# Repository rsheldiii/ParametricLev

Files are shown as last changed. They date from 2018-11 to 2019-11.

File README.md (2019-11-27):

# ParametricLev, A Parametric Acoustic Levitation Device

video of acoustic levitator test (https://www.youtube.com/watch?v=uWjfwIOMlY8)

After coming across the Instructables for [acoustic levitators](https://www.instructables.com/id/Acoustic-Levitator/) and [tractor beams](https://www.instructables.com/id/Acoustic-Tractor-Beam/) from UpnaLab, I was determined to make my own. I wanted a little more control over how the device looked, so I set about making a parametric version. Generating a new enclosure still has some manual tweaking, but it's much easier now!

# Acoustic Levitation?

I encourage you to explore the instructables linked above, but the tl;dr of acoustic levitation is by manipulating sound waves high enough that the human ear can't hear them, you can create high pressure and low pressure pockets that will force objects to move in a predictable pattern. In our case, we are setting up two transducer arrays in direct opposition to each other, creating a standing wave that will allow us to place objects at the nodes.

# Differences from the original design

## BigLev

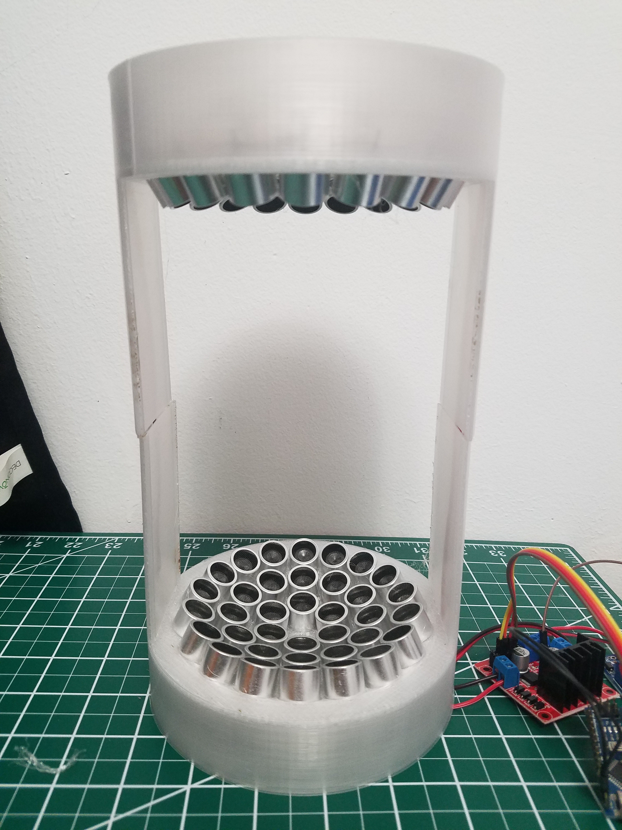
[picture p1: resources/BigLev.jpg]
picture of BigLev


Like BigLev in the instructable, I ended up going with 16mm transducers, since they are more powerful and they were also cheaper than any 12mm transducers I could find. I bought 8 of [these](https://www.amazon.com/gp/product/B01FDGTXT4/ref=oh_aui_detailpage_o00_s00?ie=UTF8&psc=1) for ~$8 a pop, for a total of 80 transducers. If you so desire, this allows you to build a BigLev, a MicroLev, and a NanoLev (72 + 6 + 2).

The original acoustic levitation instructable has you order a power supply that can discretely switch between voltages. This works well, but my transducers support up to 30 volts, so I ended up using the variable step-up transformer from the tractor beam instructable. 30 volts is overkill for most applications (since voltage is mostly related to how dense a material you can levitate) but being able to precisely tune the voltage level is great for getting things to stay stable.

## MicroLev

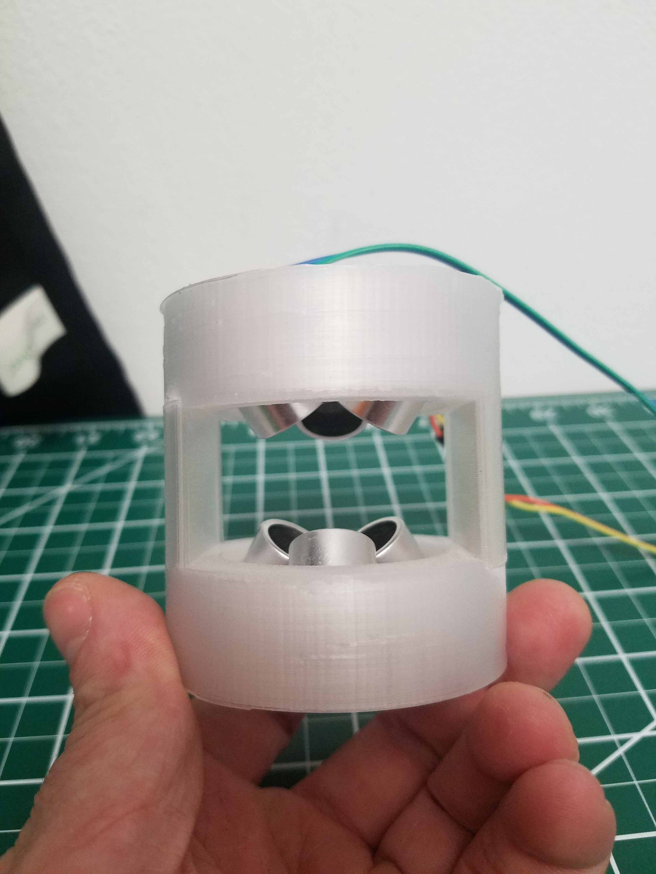
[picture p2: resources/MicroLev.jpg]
picture of MicroLev


MicroLev isn't featured in the original isntructable, but I wanted something simpler to test the wiring on before scaling all the way up. 6 transducers is a little hard for the nano to drive, so it can just barely levitate styrofoam without a motor controller. You might be able to increase this power by hooking up each transducer to a different pin and modifying the code, since you won't be reliant on the current output of a single pin to drive the transducers, but remember that arduino pins are connected to buses which themselves have a max current draw, so you'll have to be crafty about it. You can sidestep all of this however and just wire the MicroLev like you would the BigLev here or in the original instructable, allowing you to levitate popcorn pieces and probably a few other things.

## NanoLev

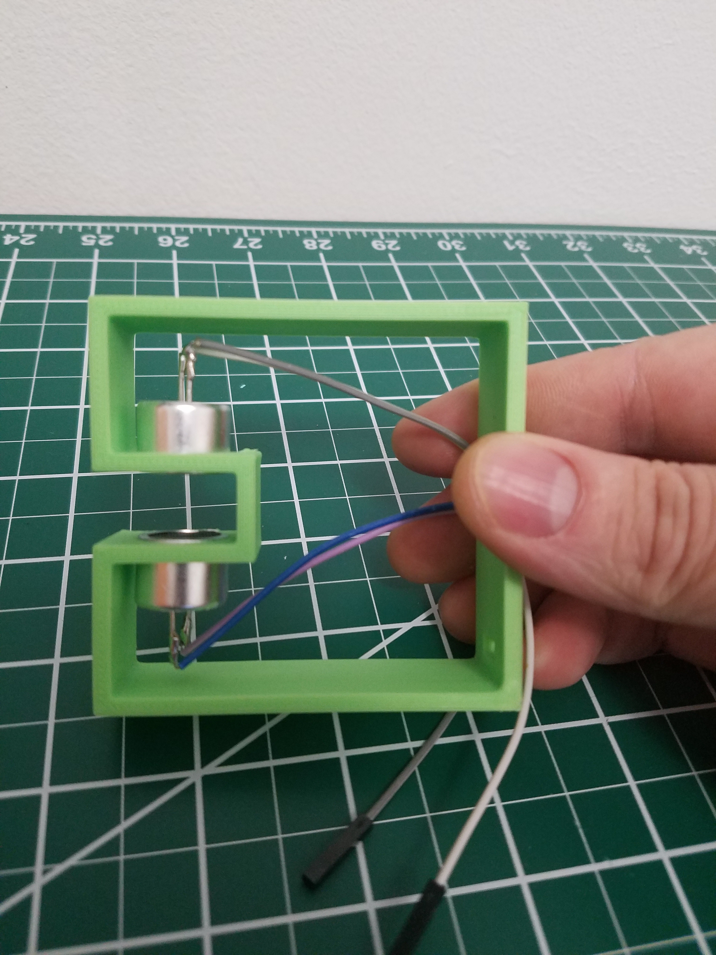
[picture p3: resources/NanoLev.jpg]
picture of NanoLev


the NanoLev is a tiny WIP enclosure for the two-transducer device from the instructable. You'll have to find something to support the Nano, but it works ok!

# How to assemble

This is only a list of the changes to the instructions and gotchas I encountered, so please reference the original instructable while you assemble the design. I may write up a full build log later, but as it stands the differences are pretty minimal

## BOM

* l298N, https://www.amazon.com/gp/product/B01CC8XI60/
* Arduino nano, https://www.amazon.com/gp/product/B00Q9YBO88/
* DC/DC Voltage Transformer, https://www.amazon.com/gp/product/B00J03PBW0
* 12V 3A wall wart, https://www.amazon.com/gp/product/B07CWVFGNN
* 72 16mm 40khz transducers, https://www.amazon.com/gp/product/B01FDGTXT4/
* bare copper wire, https://www.amazon.com/gp/product/B00E4WL2D4/
* black/red wire, https://www.amazon.com/gp/product/B009VCZ4V8/
* barrel connector, https://www.amazon.com/gp/product/B00T7VOKM2/

## Printing

for the __BigLev__, print two halves, with support. for the __MicroLev__ you need to print the top and bottom; the files come from an earlier design where opposing sides slotted together that unfortunately didn't fit on my 3d printer when scaling up to the BigLev. For the NanoLev, just print the one file; it's a completely different setup than the other designs.

There are some nasty overhangs in the BigLev and MicroLev prints, so make sure you print in whatever material gives you the best overhang performance.

## Transducers

DO NOT SKIP MARKING YOUR TRANSDUCERS. Despite most transducers having a marked 'ground' wire it does NOT correlate to polarity. For most applications this does not matter, but in our case if you place two transducers with opposite polarity next to each other they will destructively interfere, decreasing the power of your device. The direction of the polarity doesn't actually matter, but what _does_ matter is that all transducers are wired the same. I placed the marked leg towards the center, just like the instructable. I created a jig for testing the polarity, which you can glue wires into to make it easier to connect the transducer to the arduino:

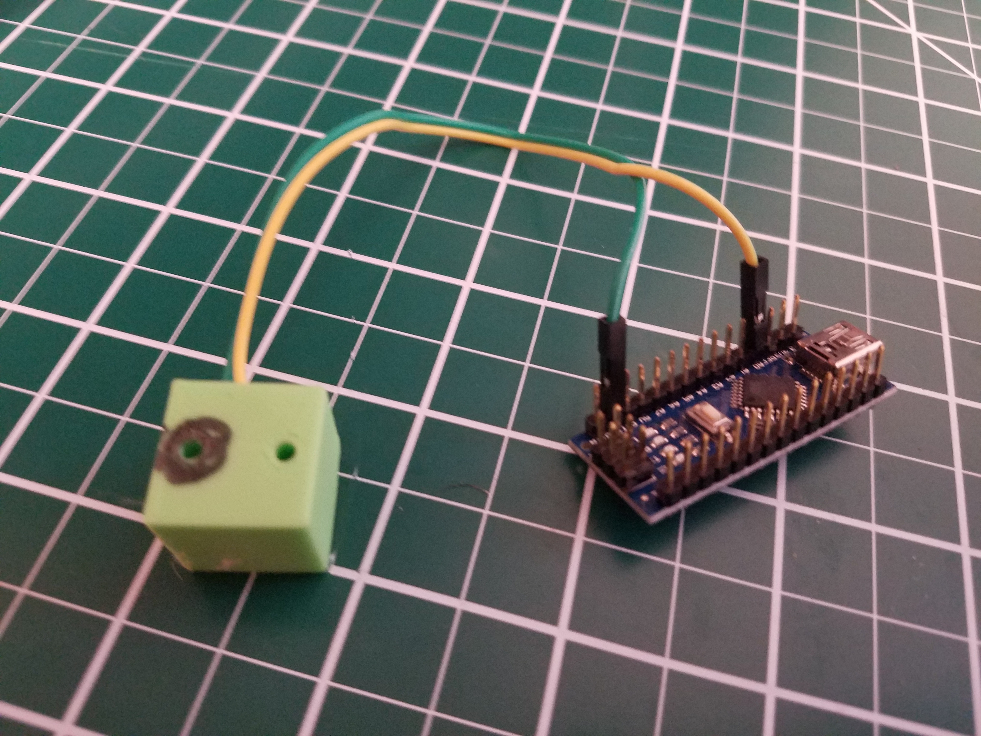
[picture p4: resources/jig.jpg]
picture of wiring jig


Most transducers come in pairs; one transducer is for transmitting waves and the other for receiving. Transmitters are tuned to produce waves based on electrical input, whereas receivers are tuned to produce electrical input based on sounds. While this _sounds_ bad for us, since we are only interested in producing waves, receivers and transmitters can be used interchangeably with a small loss in efficiency. If you can find a source of only transmitters (or transceivers, which are a compromise between the two) by all means, but it really isn't worth any extra money. For peace of mind, I separated my transmitters and receivers and alternated between them when I placed them in the enclosure, so that I wouldn't accidentally place a large amount of them on either half.

## Wiring

I will get better pictures for this later, I promise.

You can by all means follow the original wiring in the instructable, but if you want to use the step-up transformer you'll have to make a few modifications. Wire the actual device as they do in the instructable, and wire it to the l298N driver as they do as well. Since we'll be far exceeding the 12V the controller needs to run its own logic, we'll need to patch in 12V from the wall wart and tell the controller to use that for logic instead of the input voltage. This means you need to take off the jumper, and attach a wire from 12V in it's place. See the brown wire in this picture:

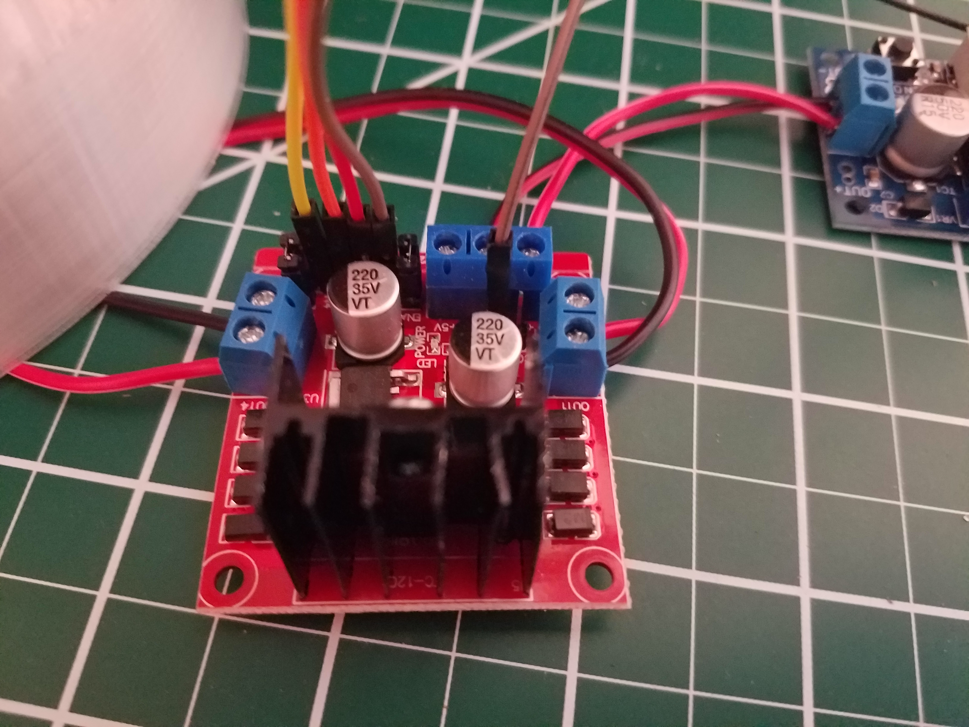
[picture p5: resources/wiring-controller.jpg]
picture of wiring the l298N controller


It is VERY IMPORTANT to put this wire in the correct place, otherwise you might damage the controller or start a fire.

Instead of feeding in electricity directly from the wall wart, the input to the controller comes from the step-up transformer, as you can see in the picture.

The arduino Nano can't handle the voltage we'll be pumping into the controller, so we'll also need to run wires from the barrel connector to the arduino's VIN and GND pins. Otherwise, the wiring is the same as the instructable. Picture reference:

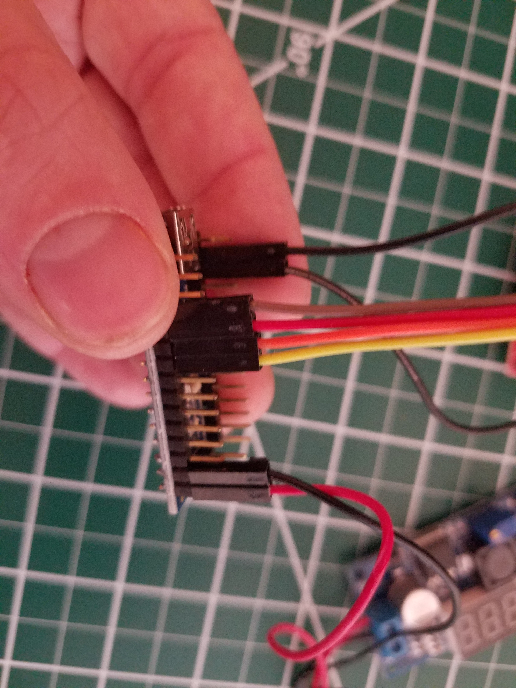
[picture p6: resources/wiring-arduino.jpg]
picture of wiring the l298N controller


after all is said and done, the wiring should look like this:

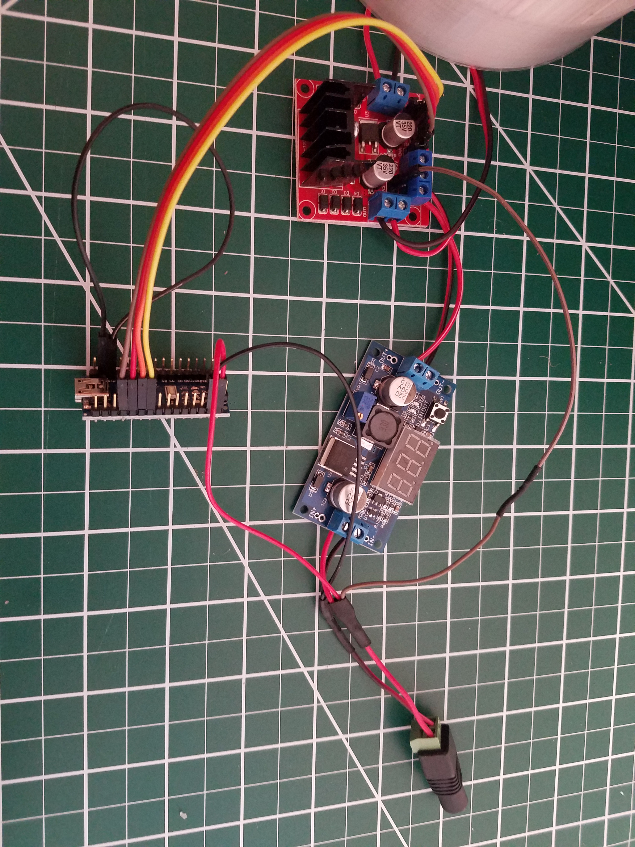
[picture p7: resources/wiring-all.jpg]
picture of wiring the l298N controller


except not as messy

## Programming

Programming on the arduino is exactly the same as in the instructable, just grab their .ino file and use it.

Of note is that an arduino nano is pretty overkill for this application, since all it's doing is creating a 40KHZ signal. The arduino could be replaced by a clock and crystal and some power management circuitry by someone more electrically inclined than I am.

## Using

I find it easiest to use teabag material to place objects, though any sonically transparent material would work fine (wire mesh is probably the best). If your item is spinning rapidly it's an indication that the standing wave is too intense for its density; try decreasing the voltage on the transformer until it slows down.

If you have a resin printer (or are ok with paying Shapeways 7.50 per part), you can get extremely tiny 3d printed models to levitate. The size of the object that can be levitated is a function of half the wavelength, so anything more than ~4.5mm in diameter is too large. Luckily that's just above the minimum size requirements for Shapeways.

## Spacing

I have noticed with my current design that I can get some nasty resonance in the exact middle spot, causing pieces to fall despite them levitating just fine in other spots. I've noticed that changing the distance between the pieces makes this go away, so I think it's a function of the radius of the internal sphere being a multiple, or perhaps an odd multiple, of half the wavelength. I've increased the multiple to 22 but haven't actually tested it yet. If you have similar problems though, you could easily print a tiny piece of the side sponsons and glue it in place, increasing the height. I've included an example shunt in the models directory, but the height of the shunt is probably better found through experimentation.

# Modifying

If you want to use a different amount of transducers or change parameters, you can clone this repository and open up `BigLev.scad` and `src/settings.scad` in OpenSCAD or whatever editor you choose. By modifying variables in `settings.scad`, you can generate a different shape.

The amount of transducers is a function of the area of the section of the sphere generated based off some napkin trig, so if you're looking for a specific amount of transducers you'll have to play around a bit (or you can try refactoring the old code in OldStuff.scad to manually control how many transducers there are). The napkin trig isn't perfect, so sometimes in order to eliminate dead space you'll have to dig into `transducers_for()` in `lev.scad` to get a more fine-tuned result. Still though, the algorithm produces good results for most cases.

## TODO

* Get better pictures!
* design a top / bottom
* refactor to allow for manual transducer placement
* refactor to allow for slop adjustments

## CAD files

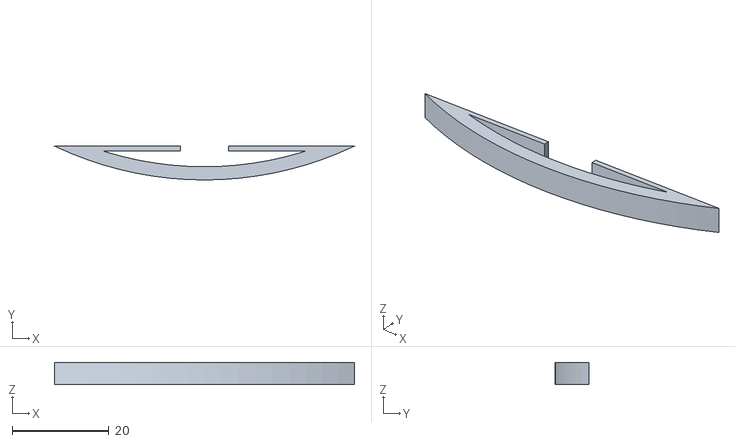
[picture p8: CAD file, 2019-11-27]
models/BigLev-shunt.stl
61.9 x 7.00 x 4.61

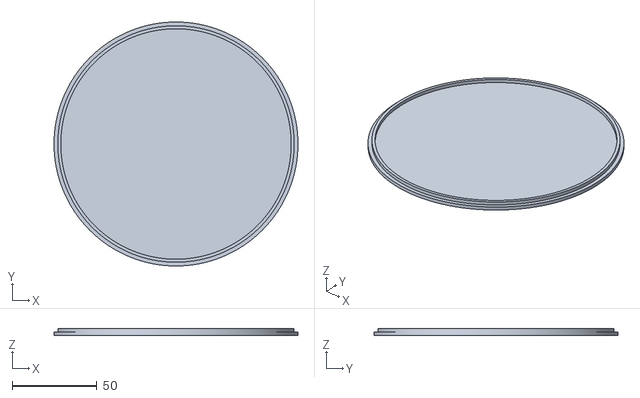
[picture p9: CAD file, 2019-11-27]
models/BigLev-top.stl
144.1 x 144.1 x 4.00

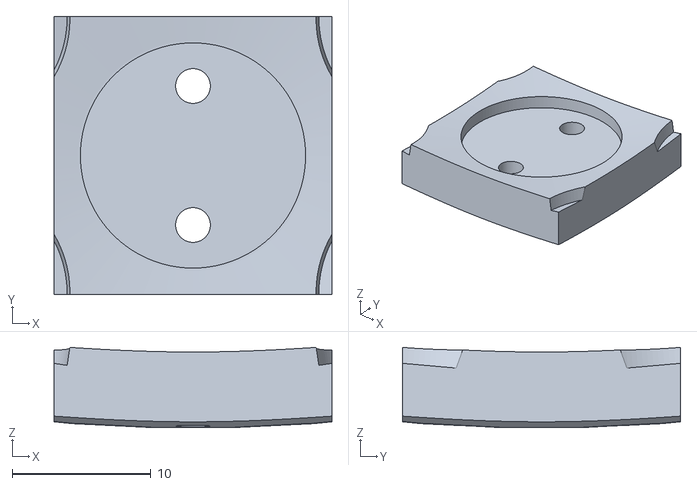
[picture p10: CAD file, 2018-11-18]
models/BigLev-test.stl
20.0 x 20.0 x 5.77

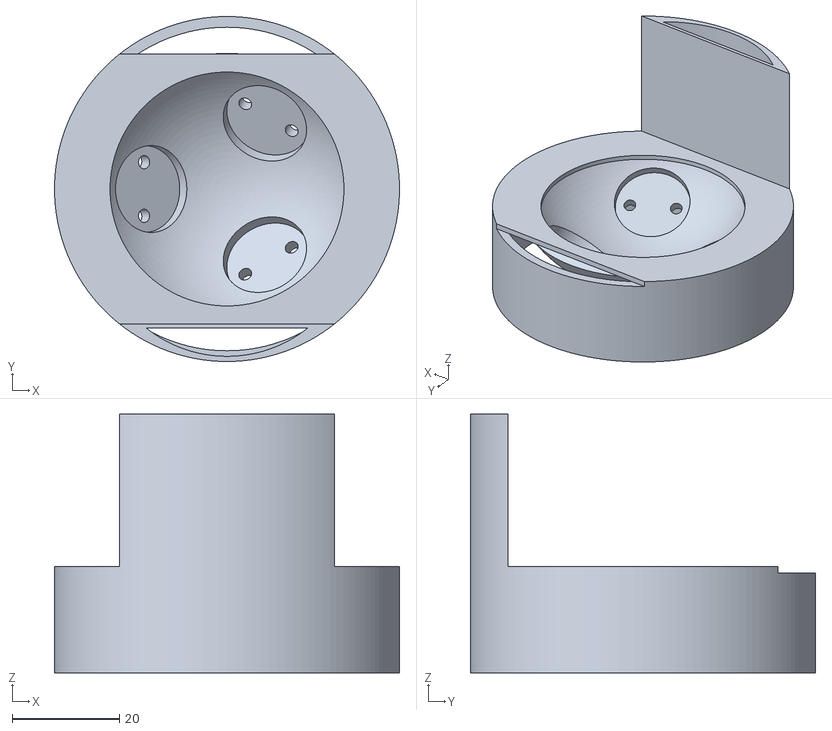
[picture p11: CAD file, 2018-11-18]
models/MicroLev.stl
64.3 x 64.3 x 48.3

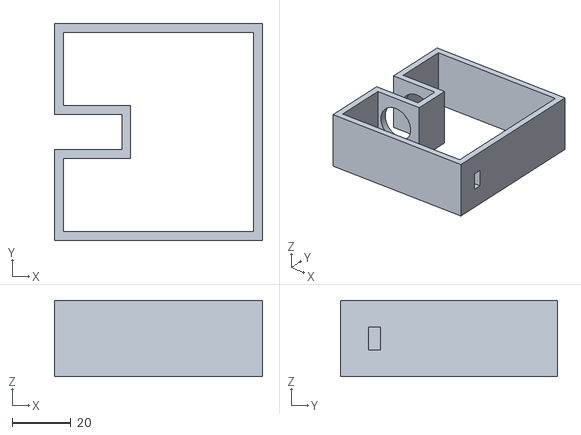
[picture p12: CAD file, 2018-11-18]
models/NanoLev.stl
71.0 x 74.0 x 26.0

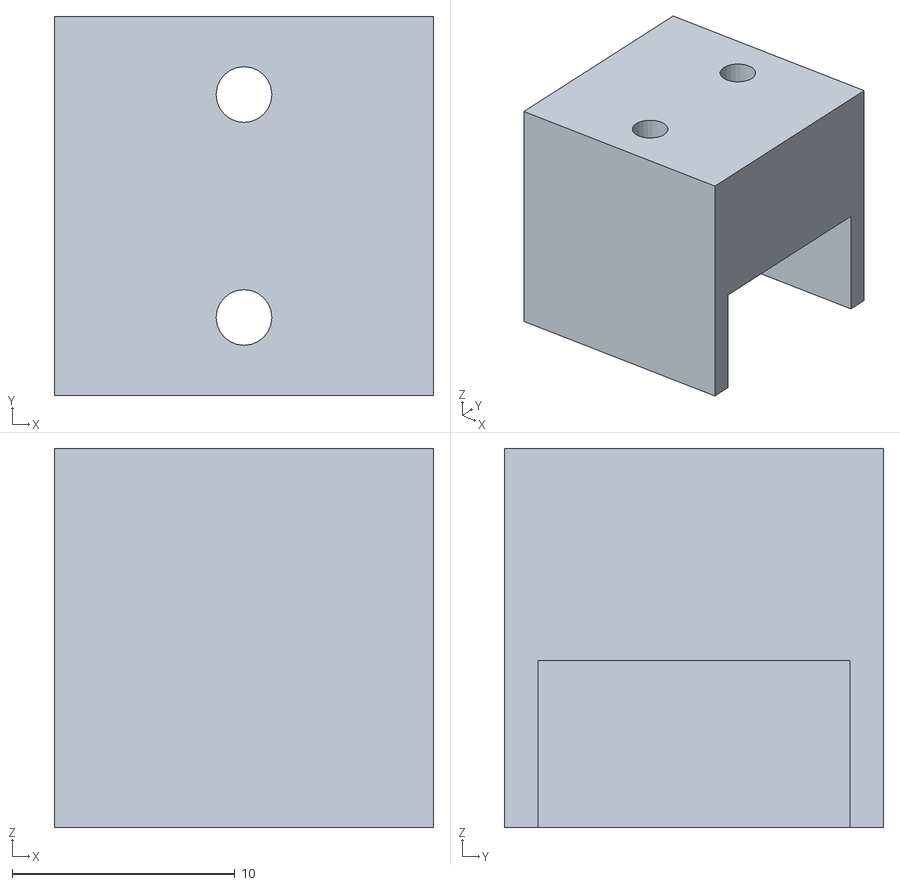
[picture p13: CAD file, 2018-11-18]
models/jig.stl
17.0 x 17.0 x 17.0

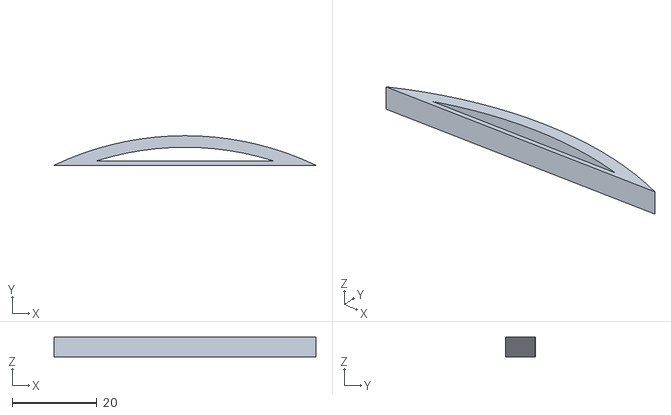
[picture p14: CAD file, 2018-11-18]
models/example-shunt.stl
61.9 x 7.00 x 4.67

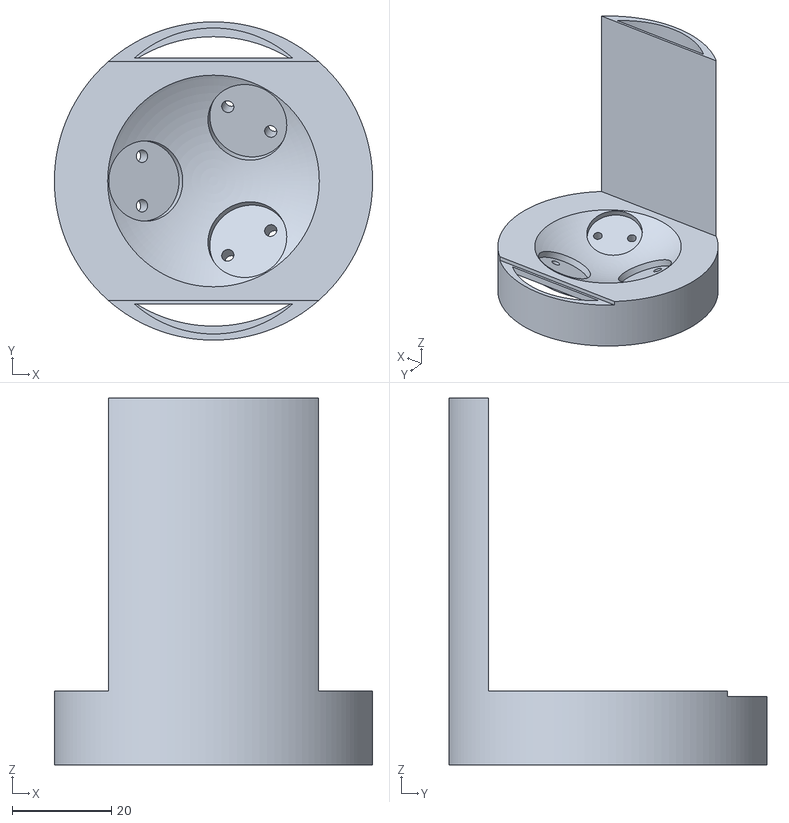
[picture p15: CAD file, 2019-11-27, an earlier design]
models/MicroLev-old.stl
64.2 x 64.2 x 74.0

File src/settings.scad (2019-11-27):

$fn=128;
// $fudge factor used strategically to eliminate crosshatching in previews without actually introducing extra play
$fudge = 0.01;

// standing nodes are made every half wavelength, so it's probably pertinent that the
// inner radius be a multiple of that
$half_wavelength = 4.68541666667;


// radius of inner sphere
$radius = $half_wavelength * 22;
// $thickness of sphere wall
$thickness = 5;

// the sphere is "cut off" - has a chunk missing - in the middle. how much is determined by this angle and some napkin trig
$end_angle = 33.109;

// how many transducers in the first ring
$start_number = 6;

// variables for the casing

$lip = 5;
$extra_room_underneath = 10;
$wall_thickness = 2;
$lip_thickness = 4;

$slop = 0.25;

// transducer settings

// 0.25 is slop for the transducers. 0.2 can sometimes yield a press fit
// I believe dollar variables that rely on other dollar variables are not recalculated so don't reassign slop unless you don't want these numbers to match up
$transducer_diameter = 16 + $slop;
$transducer_height = 12;
$transducer_leg_diameter = 2.5; // really 1mm but don't wanna skimp
$transducer_leg_separation_radius = 10 / 2;
$transducer_leg_height = 10;
$transducer_inset = 1;

// calc'ed variables
function inner_radius() = $radius;
function middle_radius() = inner_radius() + $transducer_height - $transducer_inset;
function outer_radius() = middle_radius() + $thickness;
// functions

// how far down the well is
function well_z(hypotenuse, angle) = cos(angle) * hypotenuse;
// how deep the well of transducers is
function well_depth(hypotenuse, angle) = hypotenuse - well_z(hypotenuse, angle);
// radius of the well of transducers
function well_radius(hypotenuse, angle) = sin(angle) * hypotenuse;

// what radius of circle can I place n circles of diameter d on so that they just barely don't touch?
function radius_for_circles(d, n) = 1 / (sin(180 / n)) * d / 2;
// how many circles of diameter d could fit on another circle of radius r without touching each other?
function circles_for_circumscribed_radius(r, d) = round(360 / (asin((d / 2) / r) * 2));

// if I have a chord with radius chord_r in a sphere of size r, if I were to draw a line from the bottom to the center, and then from the chord to the center, what would the angle be?
function angle_for_chord_radius(chord_r, r) = asin(chord_r / r);
// if I know the angle of a chord in a sphere, what is the chord's radius?
function chord_radius_for_angle(angle, radius) = sin(angle) * radius;
// given a side length r, what is the internal angle of the regular polygon that circumscribes that circle?
function circumscription_angle(r, s) = atan(s / 2 / r) * 2;

module transducer_placement(radius, rotation=[], inset=$transducer_inset) {
  rotate(rotation) translate([0,0,-radius - inset]) rotate(90) children();
}

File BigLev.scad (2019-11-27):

include <src/transducer.scad>
include <src/lev.scad>
include <src/case.scad>

union(){
  /* translate([0,0,0]) lev();
  outside(); */
  /* translate([0,0,40]) cube(20, center = true); */
  /* translate([0,-500, 0]) cube(1000); */
}

sponson_z = -well_z(outer_radius(), $end_angle) + $lip_thickness;


/* translate([0,0,-middle_radius()+22]) %cylinder(r=well_radius(middle_radius(), $end_angle)); */
// no idea why +1. really need to figure this out
/* translate([0,0,-$lip_thickness+1]) rotate(0) mirror([0,1,0]) { */

  outside();
  lev();
  /* total_sponson(); */
  /* rotate(180) total_sponson(); */
  /* translate([0,0,-outer_radius() - $extra_room_underneath - $wall_thickness*3]) top_cover(); */

/* } */

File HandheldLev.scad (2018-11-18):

include <src/transducer.scad>
include<src/lev.scad>
include <src/case.scad>

middle_radius() = 56; // for handheld
$thickness = 3; // for handheld
$end_angle = 75; // for handheld

// how many transducers in the first ring
$start_number = 6;

lev();

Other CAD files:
models/MicroLev-Top.stl
jig.scad
MicroLev.scad
src/OldStuff.scad
src/case.scad
src/circletest.scad
src/lev.scad
src/transducer.scad
